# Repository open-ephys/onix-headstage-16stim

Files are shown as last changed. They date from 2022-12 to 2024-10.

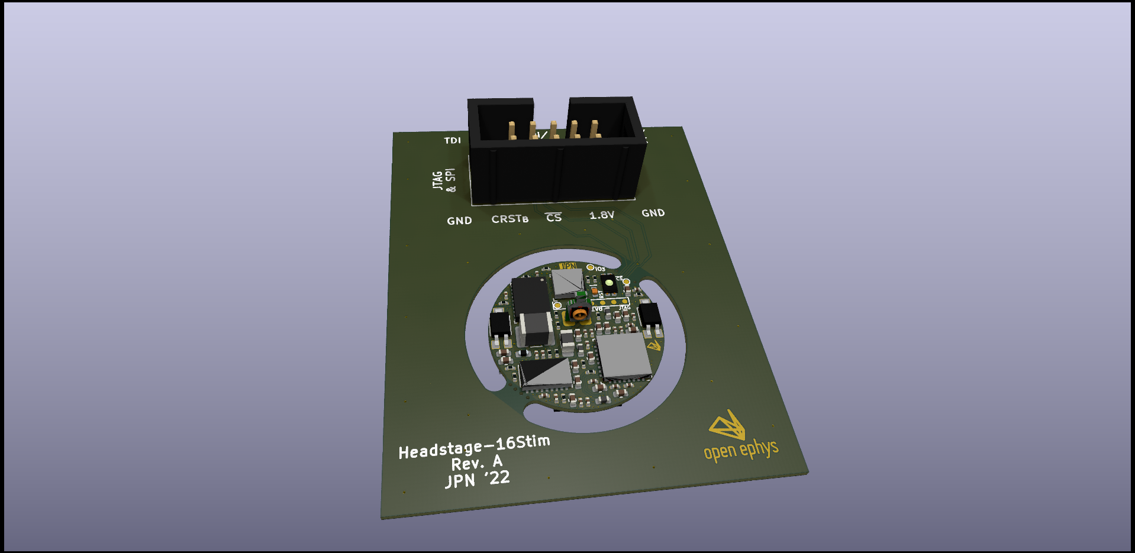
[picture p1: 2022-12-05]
pcb/manufacturing/headstage-16stim-3d-top.png

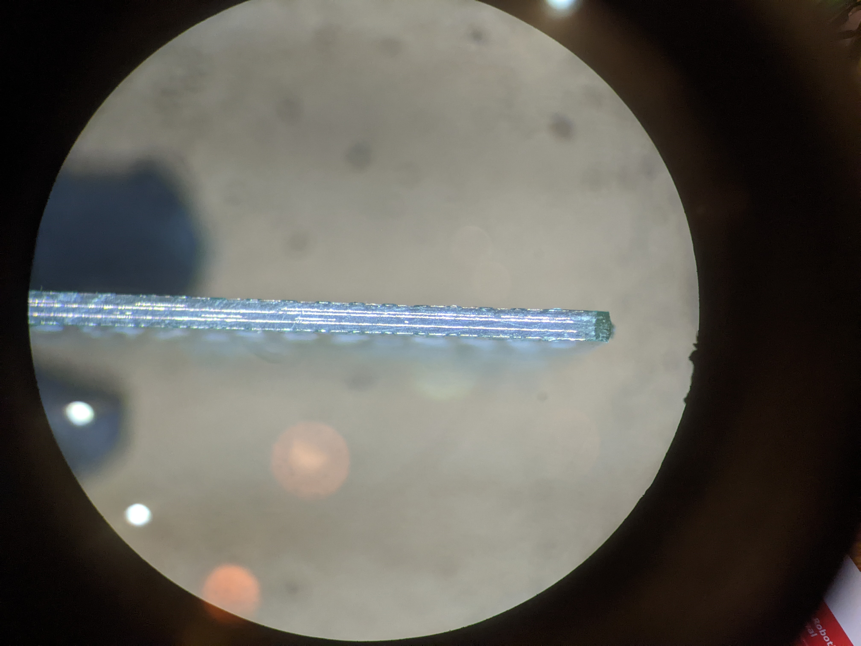
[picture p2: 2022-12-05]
pcb/manufacturing/speedy-6-layer-0.6mm.jpg

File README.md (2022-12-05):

# ONIX 16-Channel Bidirectional Headstage
Serialized, multifunction headstage for wire electrode or silicon probe recordings.

- 16x bi-directional electrophysiology channels (±7V stimulus compliance)
- Integrated stimulus sequencer and memory
- Integrated real-time, room-scale 3D-position tracking
- Integrated absolute orientation tracking

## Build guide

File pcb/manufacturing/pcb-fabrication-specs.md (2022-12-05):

# PCB Fabrication Specifications

## Single board Dimensions
- Width: 40.0000 mm
- Height: 51.0000 mm
- Area: 2040.0000 sq. mm

## Panel
- Fabricator makes panel as 1x5 with V-Cuts
- Fabricator adds frame and fiducial marks
- Fabricator markings allowed on frame

## Stackup
- layer "F.Cu" 
    - type "copper" 
    - Thickness 0.035 mm
- layer "Dielectric 1" 
    - type "prepreg" 
    - Thickness 0.112 mm 
- layer "In1.Cu" 
    - type "copper" 
    - Thickness 0.035 mm
- layer "Dielectric 2" 
    - type "prepreg" 
    - Thickness 0.0329 mm 
- layer "In2.Cu" 
    - type "copper" 
    - Thickness 0.035 mm
- layer "Dielectric 3" 
    - type "core" 
    - Thickness 0.0656 mm 
- layer "In3.Cu" 
    - type "copper" 
    - Thickness 0.035 mm
- layer "Dielectric 4" 
    - type "prepreg" 
    - Thickness 0.0329 mm 
- layer "In4.Cu" 
    - type "copper" 
    - Thickness 0.035 mm
- layer "Dielectric 5" 
    - type "prepreg 
    - Thickness 0.112 mm 
- layer "B.Cu" 
    - type "copper" 
    - Thickness 0.035 mm

- Total thickness: ~0.6mm

## Trace space
- Trace: 0.0762 mm
- Space: 0.0762 mm

## Vias
- Through vias: 232
- Blind/buried: 0
- Micro vias: 0
- VIP
- Vias are epoxy-filled and and plated over

## Drill holes
| Count | Shape |    X Size |    Y Size | Plated | Via/Pad | Start Layer | Stop Layer |
|-------|-------|-----------|-----------|--------|---------|-------------|------------|
|   192 | Round | 0.1000 mm | 0.1000 mm |    PTH |     Via |        F.Cu |       B.Cu |
|    40 | Round | 0.2000 mm | 0.2000 mm |    PTH |     Via |        F.Cu |       B.Cu |
|    10 | Round | 1.0000 mm | 1.0000 mm |    PTH |     Pad |        F.Cu |       B.Cu |

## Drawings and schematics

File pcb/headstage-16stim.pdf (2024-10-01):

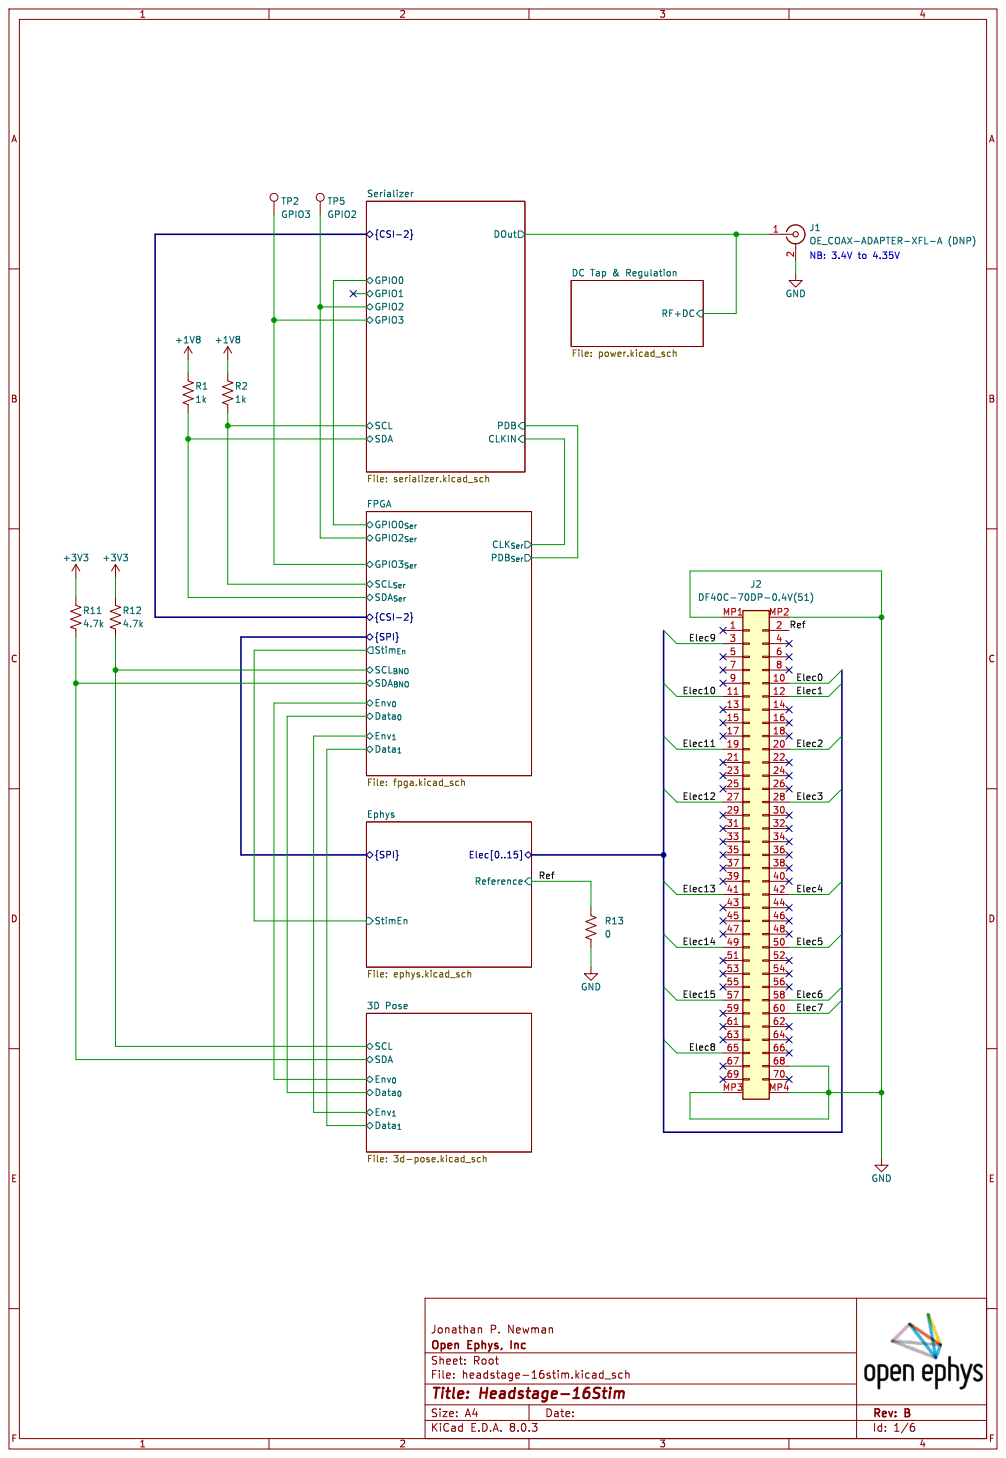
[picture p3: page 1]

{CSI-2} GPIO2 GPIO1 Serializer File: serializer.kicad_sch R11

DC Tap & Regulation File: power.kicad_sch

Data_{1} 3D Pose File: 3d-pose.kicad_sch Reference

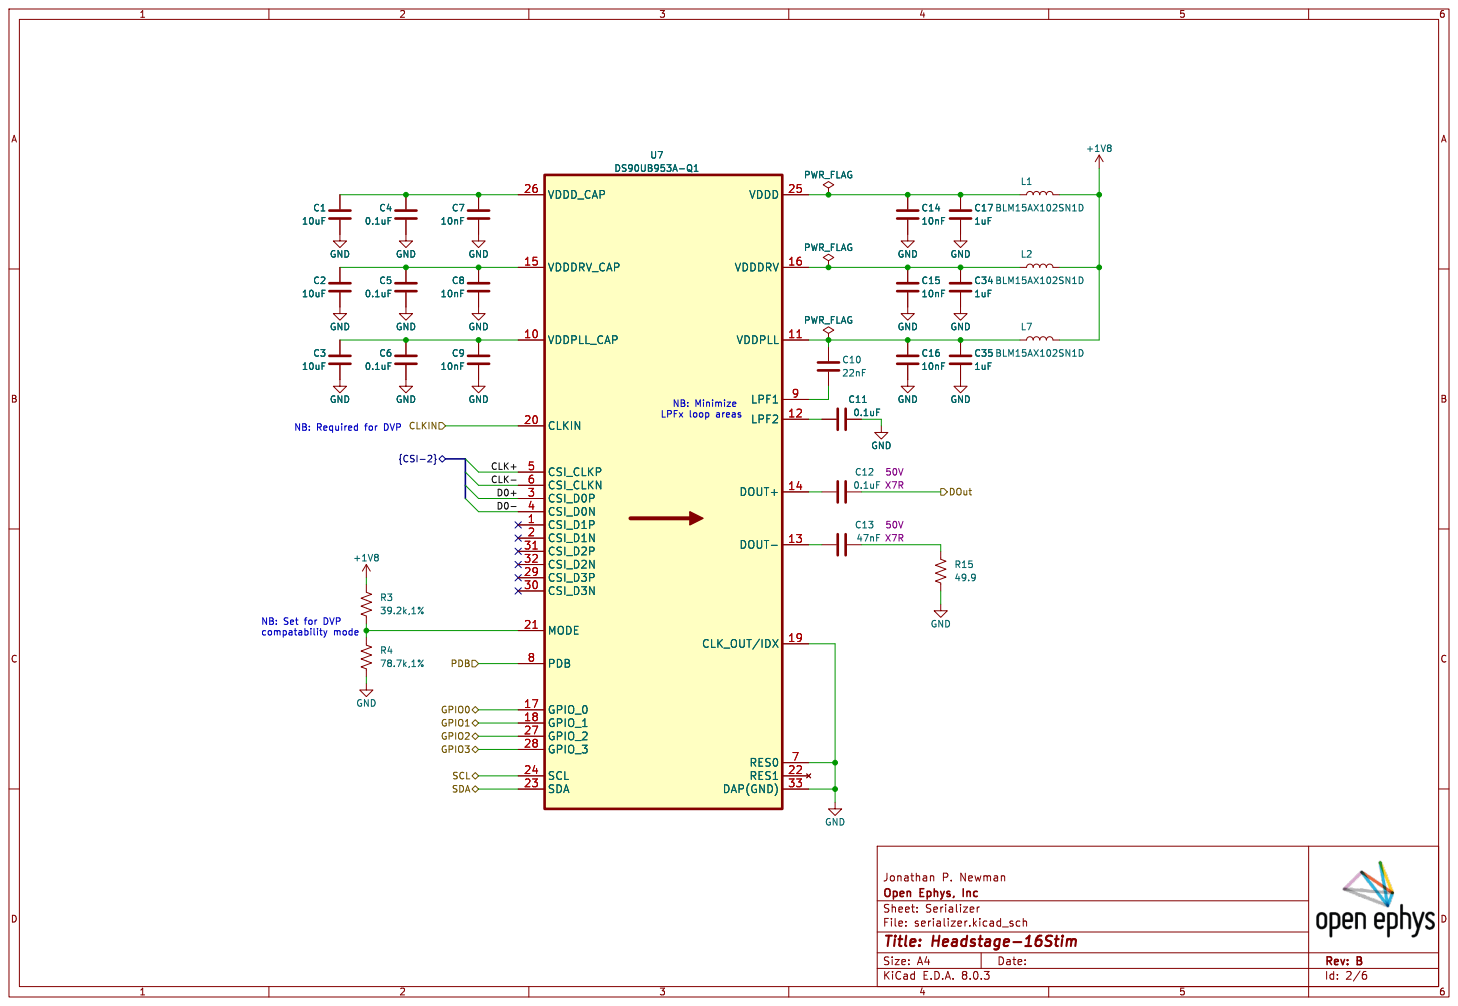
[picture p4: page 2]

LPFx loop areas NB: Set for DVP

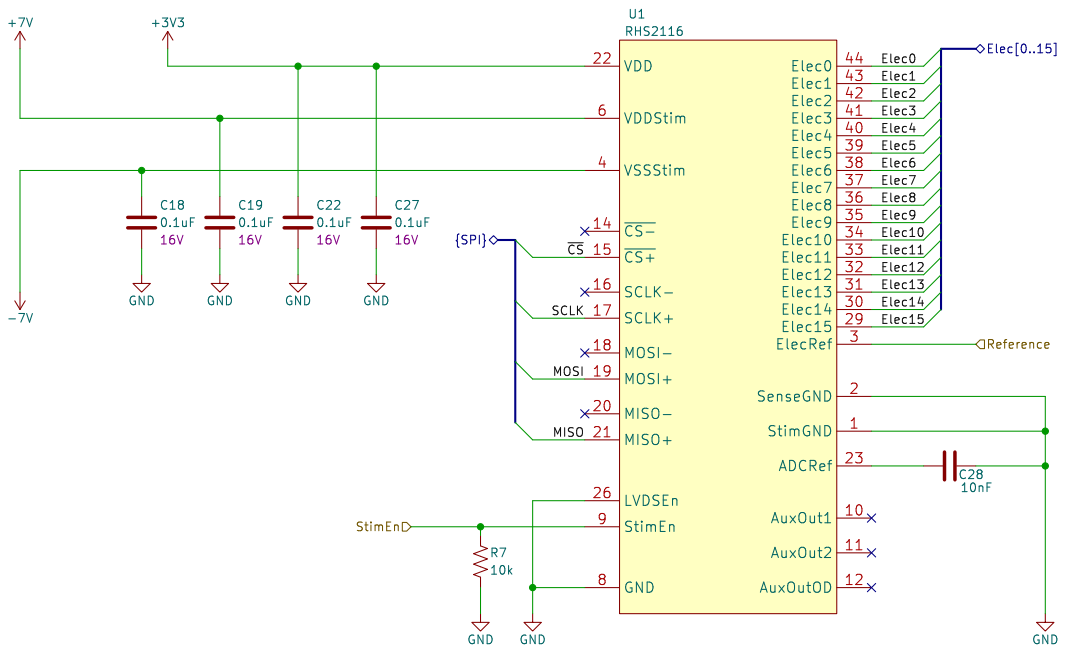
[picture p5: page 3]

File: ephys.kicad_sch Sheet: Ephys
Id: 3/6 Title: Headstage-16Stim

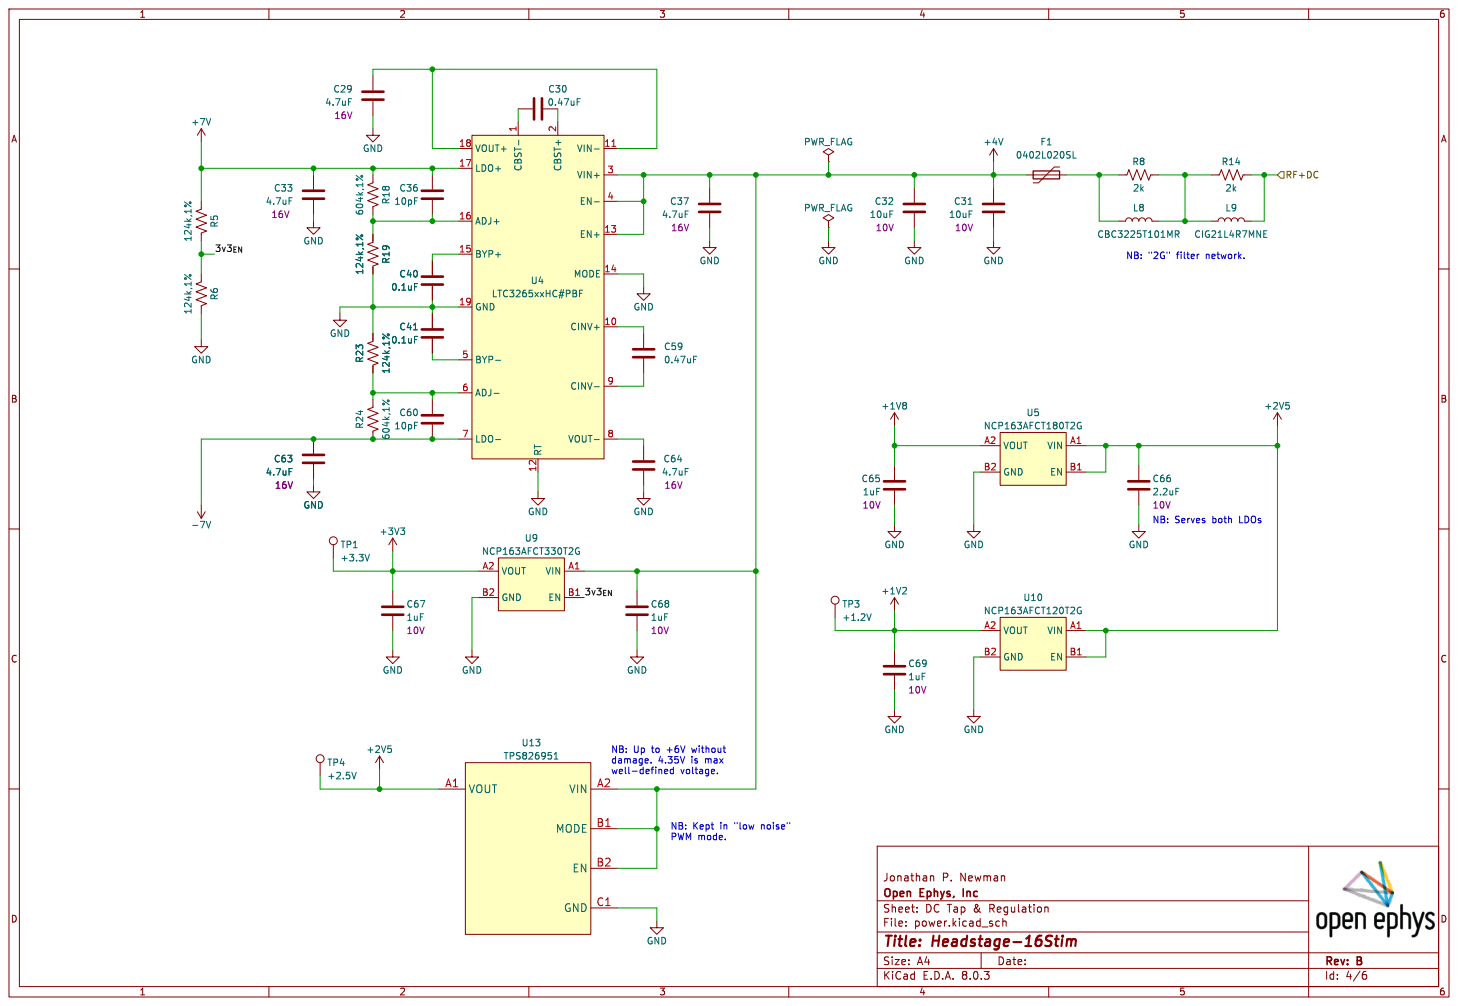
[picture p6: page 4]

2 VIN+ 3 EN- 4 BYP- 5 ADJ- 6

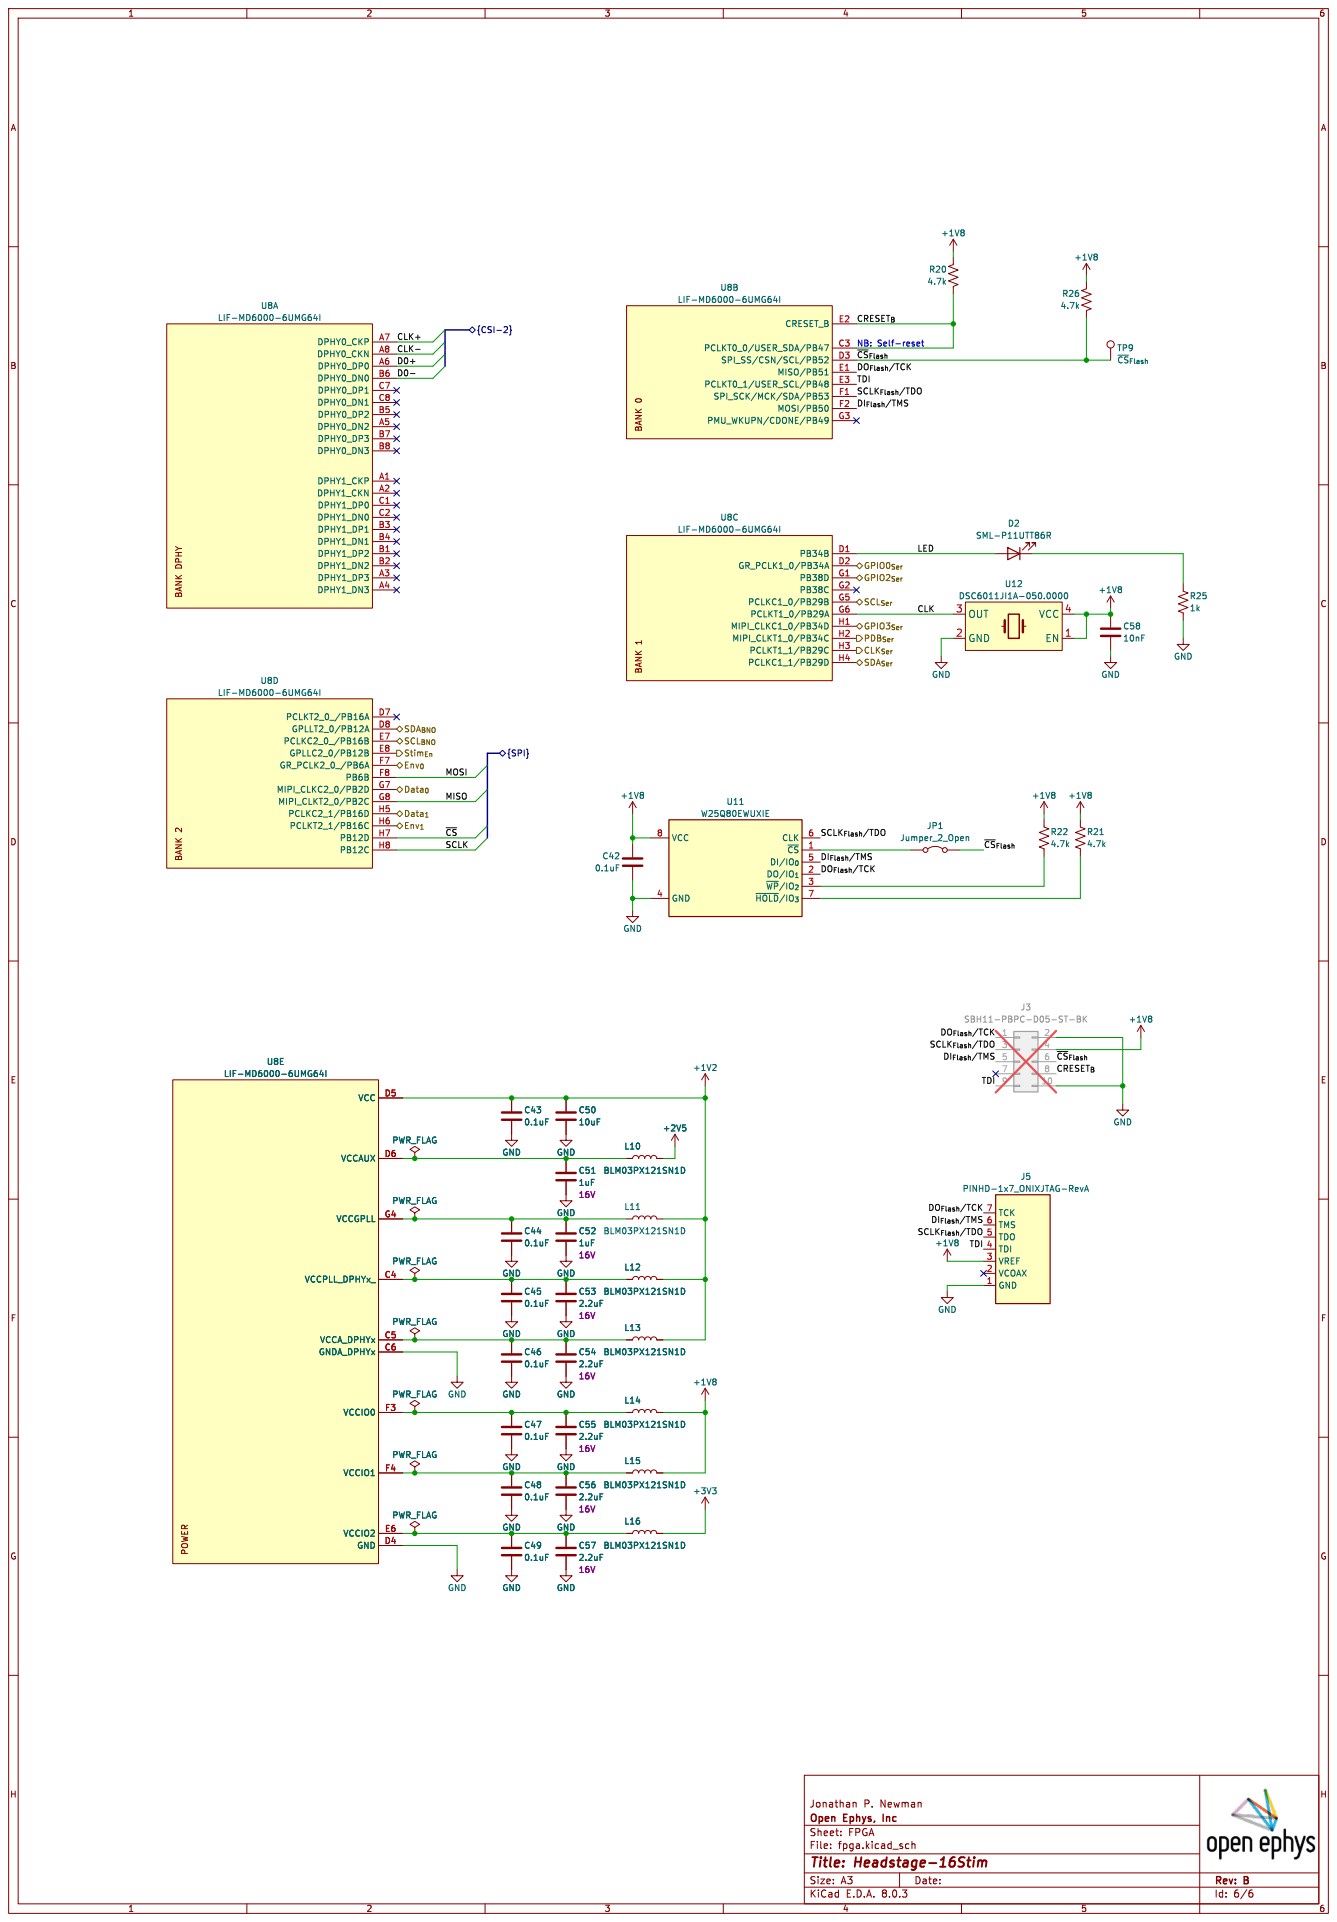
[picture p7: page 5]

CRESET_{B} LED MISO MOSI SCLK

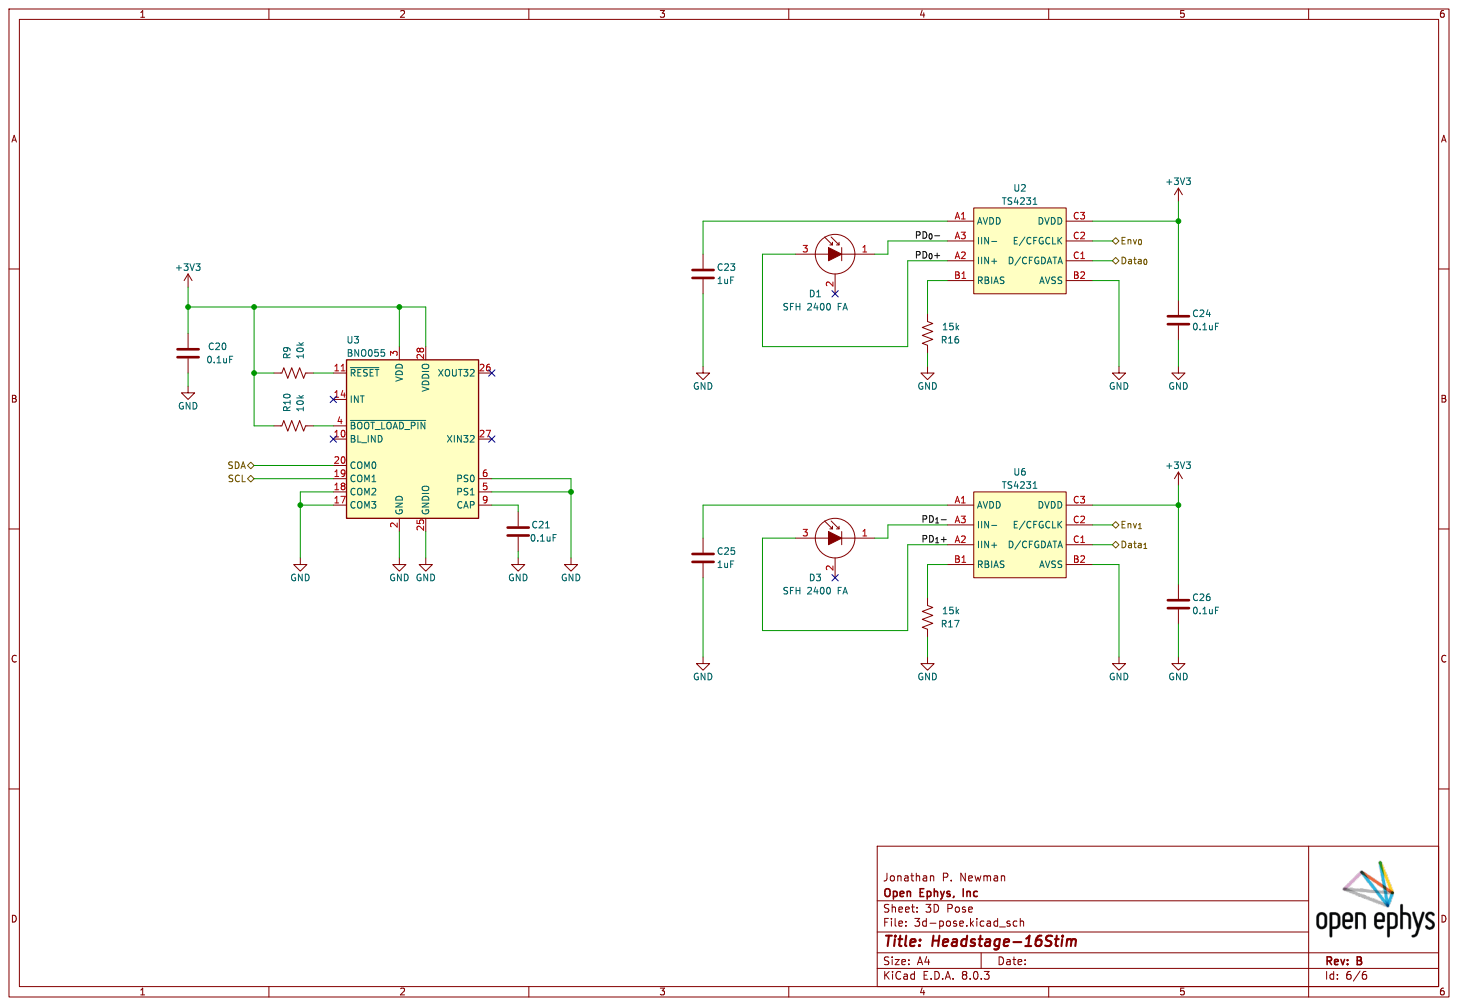
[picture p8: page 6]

3 ~{BOOT_LOAD_PIN} 4 PS1 5 PS0 6 CAP 9 U3BNO055 +3V3 R10 10k GND GND GND GND

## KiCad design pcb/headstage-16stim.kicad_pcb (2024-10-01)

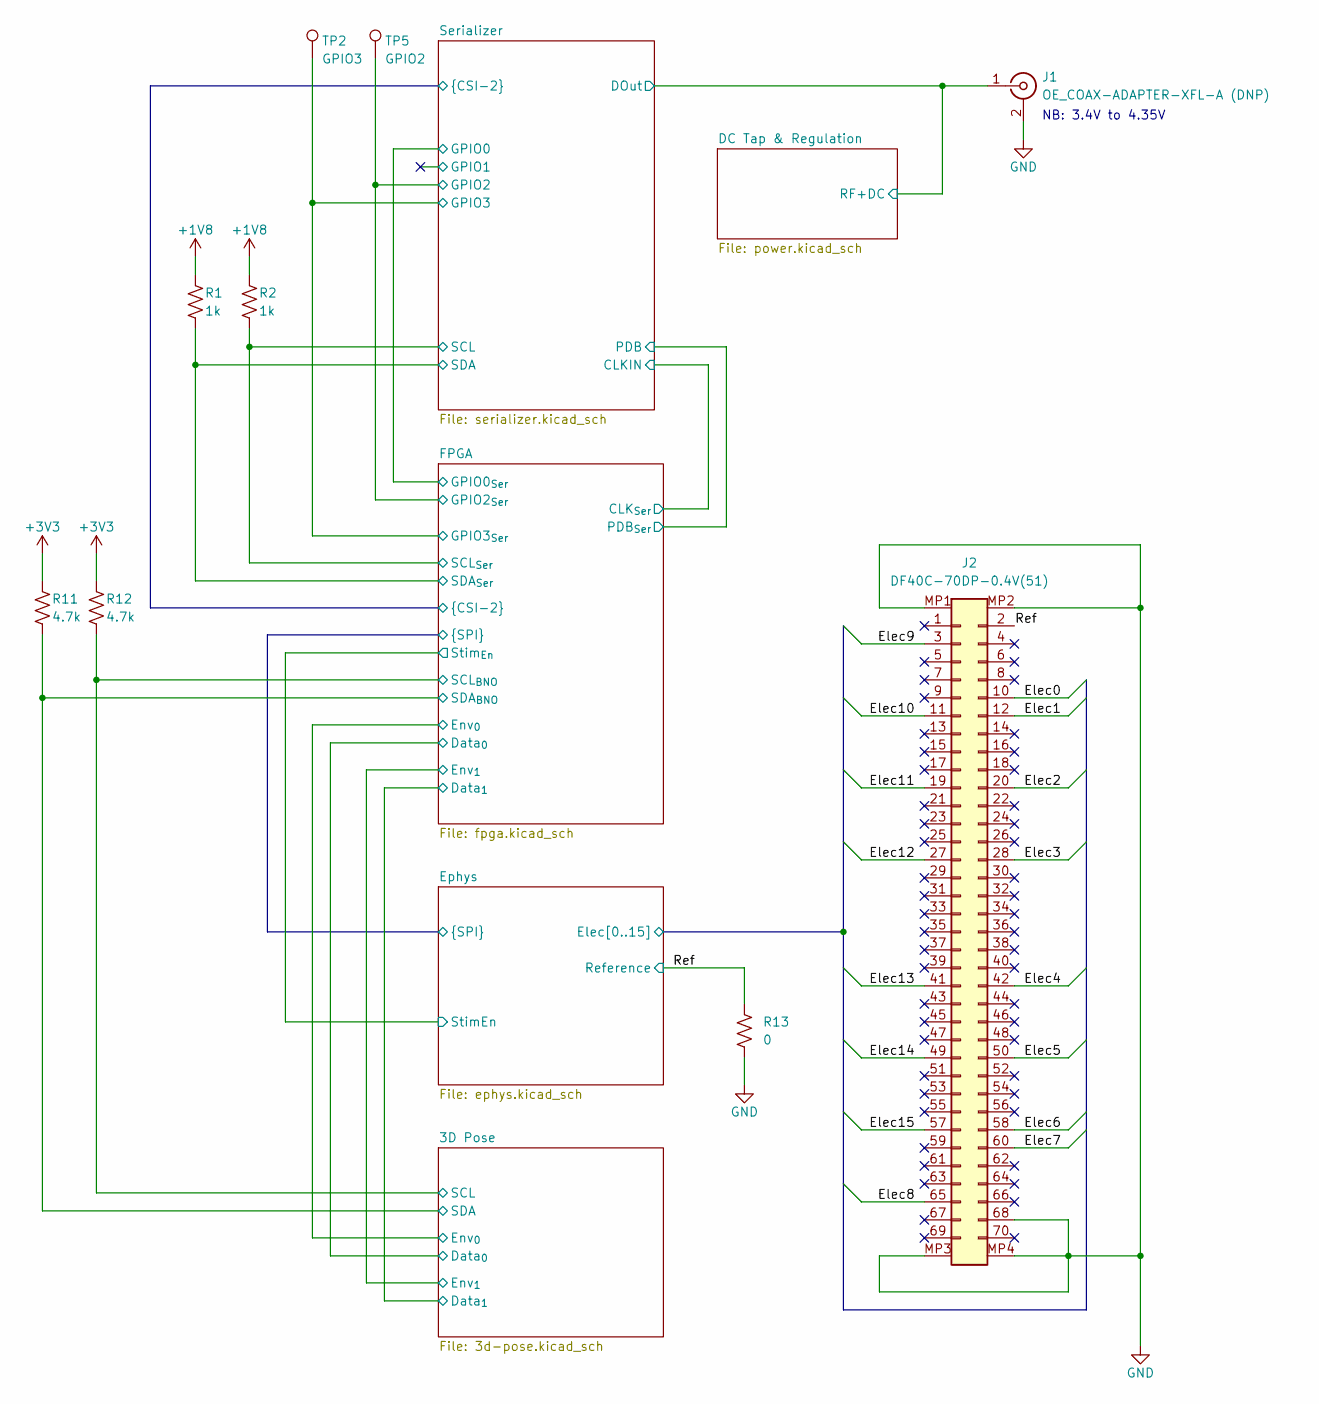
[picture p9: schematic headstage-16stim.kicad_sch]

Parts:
J1: OE_COAX-ADAPTER-XFL-A (DNP); OE_COAX-ADAPTER-XFL-A
J2: DF40C-70DP-0.4V(51); HIROSE_DF40C70DP04V51
R1, R2: 1k; R_0201_0603Metric
R11, R12: 4.7k; R_0201_0603Metric
R13: 0; R_0201_0603Metric
TP2: GPIO3; TestPoint_Pad_D0.6mm
TP5: GPIO2; TestPoint_Pad_D0.6mm

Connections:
+1V8: R1.1, R2.1; also elsewhere on the board
+3V3: R11.1, R12.1; also elsewhere on the board
/3D Pose/SCL: R12.2; also elsewhere on the board
/3D Pose/SDA: R11.2; also elsewhere on the board
/DC Tap & Regulation/RF+DC: J1.1 (In); also elsewhere on the board
/Ephys/Elec0: J2.10; also elsewhere on the board
/Ephys/Elec1: J2.12; also elsewhere on the board
/Ephys/Elec2: J2.20; also elsewhere on the board
/Ephys/Elec3: J2.28; also elsewhere on the board
/Ephys/Elec4: J2.42; also elsewhere on the board
/Ephys/Elec5: J2.50; also elsewhere on the board
/Ephys/Elec6: J2.58; also elsewhere on the board
/Ephys/Elec7: J2.60; also elsewhere on the board
/Ephys/Elec8: J2.65; also elsewhere on the board
/Ephys/Elec9: J2.3; also elsewhere on the board
/Ephys/Elec10: J2.11; also elsewhere on the board
/Ephys/Elec11: J2.19; also elsewhere on the board
/Ephys/Elec12: J2.27; also elsewhere on the board
/Ephys/Elec13: J2.41; also elsewhere on the board
/Ephys/Elec14: J2.49; also elsewhere on the board
/Ephys/Elec15: J2.57; also elsewhere on the board
/FPGA/GPIO2_{Ser}: TP5.1; also elsewhere on the board
/FPGA/GPIO3_{Ser}: TP2.1; also elsewhere on the board
/FPGA/SCL_{Ser}: R2.2; also elsewhere on the board
/FPGA/SDA_{Ser}: R1.2; also elsewhere on the board
/Ref: J2.2, R13.1; also elsewhere on the board
GND: J1.2 (Ext), J2.68, J2.MP1 (MountPin1), J2.MP2 (MountPin2), J2.MP3 (MountPin3), J2.MP4 (MountPin4), R13.2; also elsewhere on the board

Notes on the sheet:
NB: 3.4V to 4.35V

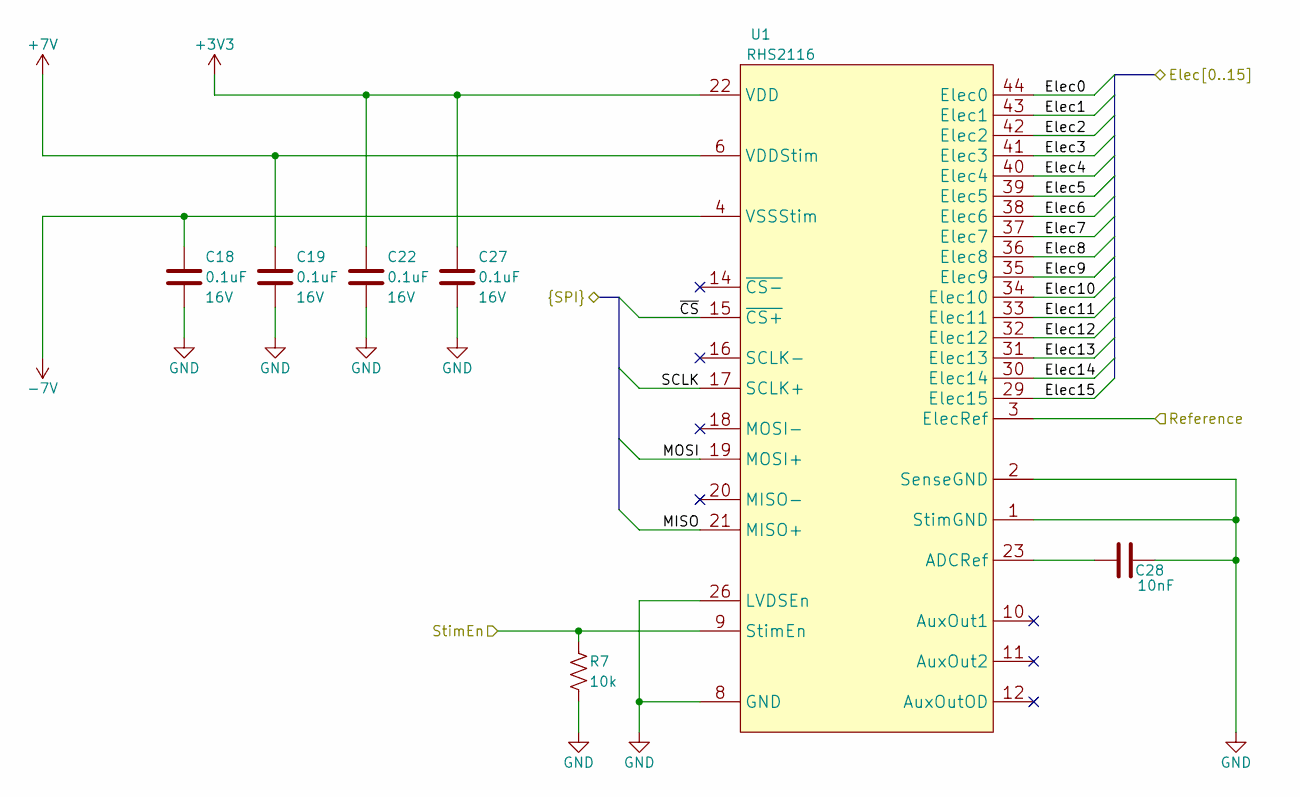
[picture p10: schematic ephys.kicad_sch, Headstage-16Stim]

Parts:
C18, C19, C22, C27: 0.1uF; C_0201_0603Metric; Voltage 16V
C28: 10nF; C_0201_0603Metric; Voltage 35V
R7: 10k; R_0201_0603Metric
U1: RHS2116; INTAN_QFN44-7.0x7.0x0.8_P0.5

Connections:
+3V3: C22.1, C27.1, U1.22 (VDD), U1.27 (VDD), U1.28 (VDD); also elsewhere on the board
+7V: C19.1, U1.6 (VDDStim), U1.7 (VDDStim); also elsewhere on the board
-7V: C18.1, U1.4 (VSSStim), U1.5 (VSSStim), U1.45 (VSSStim); also elsewhere on the board
/Ephys/Elec0: U1.44 (Elec0); also elsewhere on the board
/Ephys/Elec1: U1.43 (Elec1); also elsewhere on the board
/Ephys/Elec2: U1.42 (Elec2); also elsewhere on the board
/Ephys/Elec3: U1.41 (Elec3); also elsewhere on the board
/Ephys/Elec4: U1.40 (Elec4); also elsewhere on the board
/Ephys/Elec5: U1.39 (Elec5); also elsewhere on the board
/Ephys/Elec6: U1.38 (Elec6); also elsewhere on the board
/Ephys/Elec7: U1.37 (Elec7); also elsewhere on the board
/Ephys/Elec8: U1.36 (Elec8); also elsewhere on the board
/Ephys/Elec9: U1.35 (Elec9); also elsewhere on the board
/Ephys/Elec10: U1.34 (Elec10); also elsewhere on the board
/Ephys/Elec11: U1.33 (Elec11); also elsewhere on the board
/Ephys/Elec12: U1.32 (Elec12); also elsewhere on the board
/Ephys/Elec13: U1.31 (Elec13); also elsewhere on the board
/Ephys/Elec14: U1.30 (Elec14); also elsewhere on the board
/Ephys/Elec15: U1.29 (Elec15); also elsewhere on the board
/Ephys/MISO: U1.21 (MISO+); also elsewhere on the board
/Ephys/MOSI: U1.19 (MOSI+); also elsewhere on the board
/Ephys/SCLK: U1.17 (SCLK+); also elsewhere on the board
/Ephys/StimEn: R7.1, U1.9 (StimEn); also elsewhere on the board
/Ephys/~CS: U1.15 (~CS+); also elsewhere on the board
/Ref: U1.3 (ElecRef); also elsewhere on the board
GND: C18.2, C19.2, C22.2, C27.2, C28.2, R7.2, U1.1 (StimGND), U1.2 (SenseGND), U1.8 (GND), U1.13 (GND), U1.24 (GND), U1.25 (GND), U1.26 (LVDSEn); also elsewhere on the board
unnamed: C28.1, U1.23 (ADCRef)

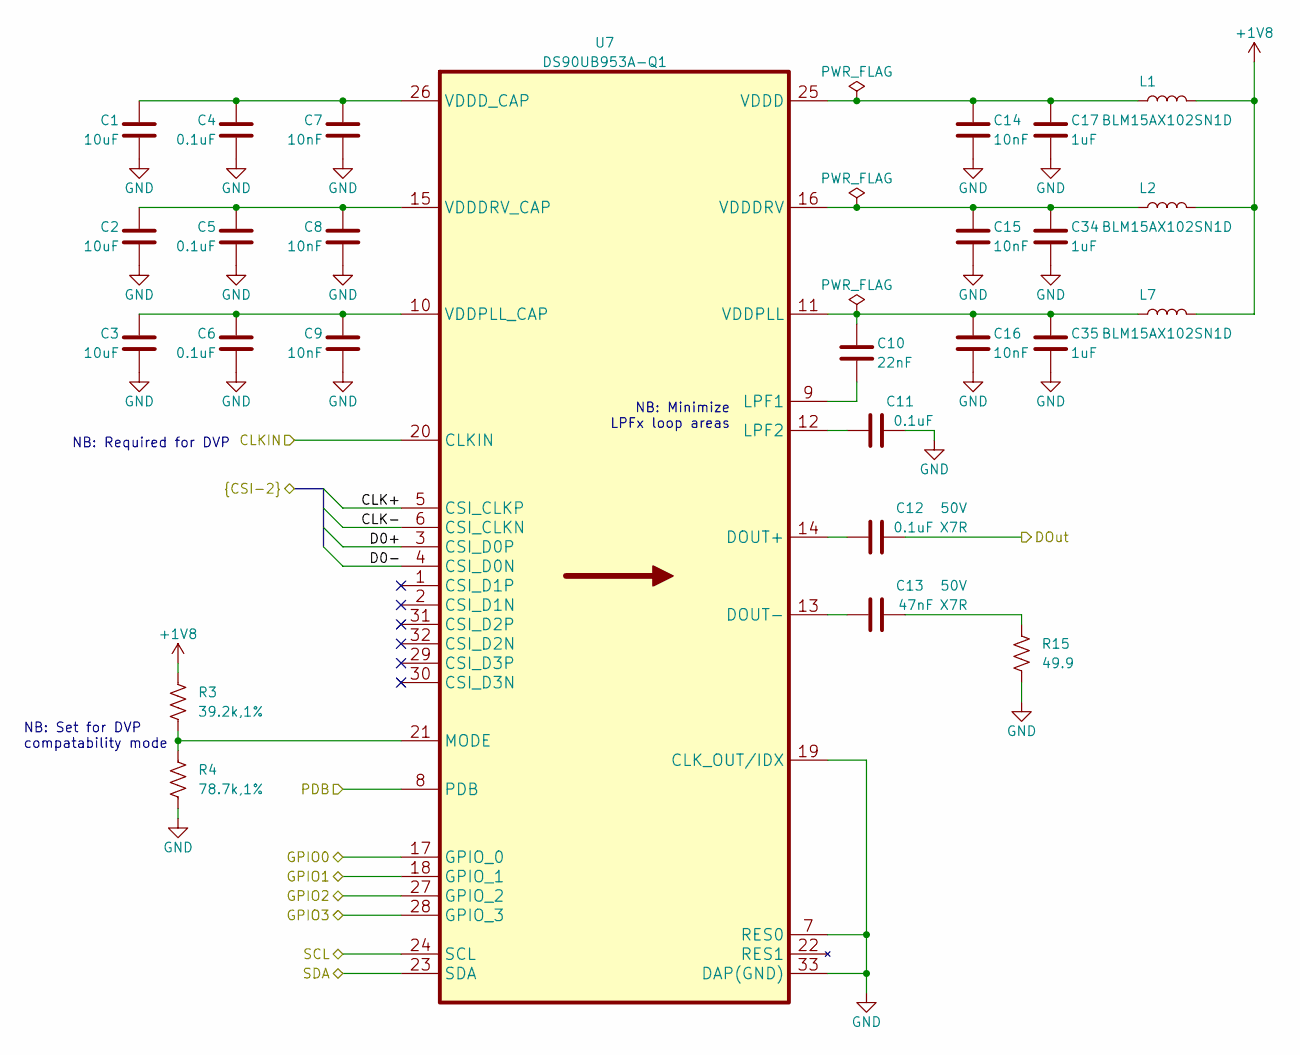
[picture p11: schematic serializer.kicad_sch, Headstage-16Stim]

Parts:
C1, C2, C3: 10uF; C_0402_1005Metric; Voltage 10V
C4, C5, C6, C11: 0.1uF; C_0201_0603Metric; Voltage 16V
C7, C8, C9, C14, C15, C16: 10nF; C_0201_0603Metric; Voltage 35V
C10: 22nF; C_0402_1005Metric; Voltage 35V
C12: 0.1uF; C_0402_1005Metric; Voltage 50V
C13: 47nF; C_0402_1005Metric; Voltage 50V
C17, C34, C35: 1uF; C_0402_1005Metric; Voltage 16V
L1, L2, L7: BLM15AX102SN1D; L_0402_1005Metric
R3: 39.2k,1%; R_0201_0603Metric
R4: 78.7k,1%; R_0201_0603Metric
R15: 49.9; R_0201_0603Metric
U7: DS90UB953A-Q1; TI_RHB0032P

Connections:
+1V8: L1.2, L2.2, L7.2, R3.1; also elsewhere on the board
/DC Tap & Regulation/RF+DC: C12.2; also elsewhere on the board
/FPGA/CLK+: U7.5 (CSI_CLKP); also elsewhere on the board
/FPGA/CLK-: U7.6 (CSI_CLKN); also elsewhere on the board
/FPGA/CLK_{Ser}: U7.20 (CLKIN); also elsewhere on the board
/FPGA/D0+: U7.3 (CSI_D0P); also elsewhere on the board
/FPGA/D0-: U7.4 (CSI_D0N); also elsewhere on the board
/FPGA/GPIO0_{Ser}: U7.17 (GPIO_0); also elsewhere on the board
/FPGA/GPIO2_{Ser}: U7.27 (GPIO_2); also elsewhere on the board
/FPGA/GPIO3_{Ser}: U7.28 (GPIO_3); also elsewhere on the board
/FPGA/PDB_{Ser}: U7.8 (PDB); also elsewhere on the board
/FPGA/SCL_{Ser}: U7.24 (SCL); also elsewhere on the board
/FPGA/SDA_{Ser}: U7.23 (SDA); also elsewhere on the board
/Serializer/GPIO1: U7.18 (GPIO_1)
GND: C1.2, C2.2, C3.2, C4.2, C5.2, C6.2, C7.2, C8.2, C9.2, C11.2, C14.2, C15.2, C16.2, C17.2, C34.2, C35.2, R4.2, R15.2, U7.7 (RES0), U7.19 (CLK_OUT/IDX), U7.33 (DAP(GND)); also elsewhere on the board
unnamed: C13.2, R15.1
unnamed: C12.1, U7.14 (DOUT+)
unnamed: C13.1, U7.13 (DOUT-)
unnamed: C10.2, U7.9 (LPF1)
unnamed: C11.1, U7.12 (LPF2)
unnamed: R3.2, R4.1, U7.21 (MODE)
unnamed: C14.1, C17.1, L1.1, U7.25 (VDDD)
unnamed: C15.1, C34.1, L2.1, U7.16 (VDDDRV)
unnamed: C2.1, C5.1, C8.1, U7.15 (VDDDRV_CAP)
unnamed: C1.1, C4.1, C7.1, U7.26 (VDDD_CAP)
unnamed: C10.1, C16.1, C35.1, L7.1, U7.11 (VDDPLL)
unnamed: C3.1, C6.1, C9.1, U7.10 (VDDPLL_CAP)

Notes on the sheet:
NB: Set for DVP compatability mode
NB: Required for DVP
NB: Minimize LPFx loop areas

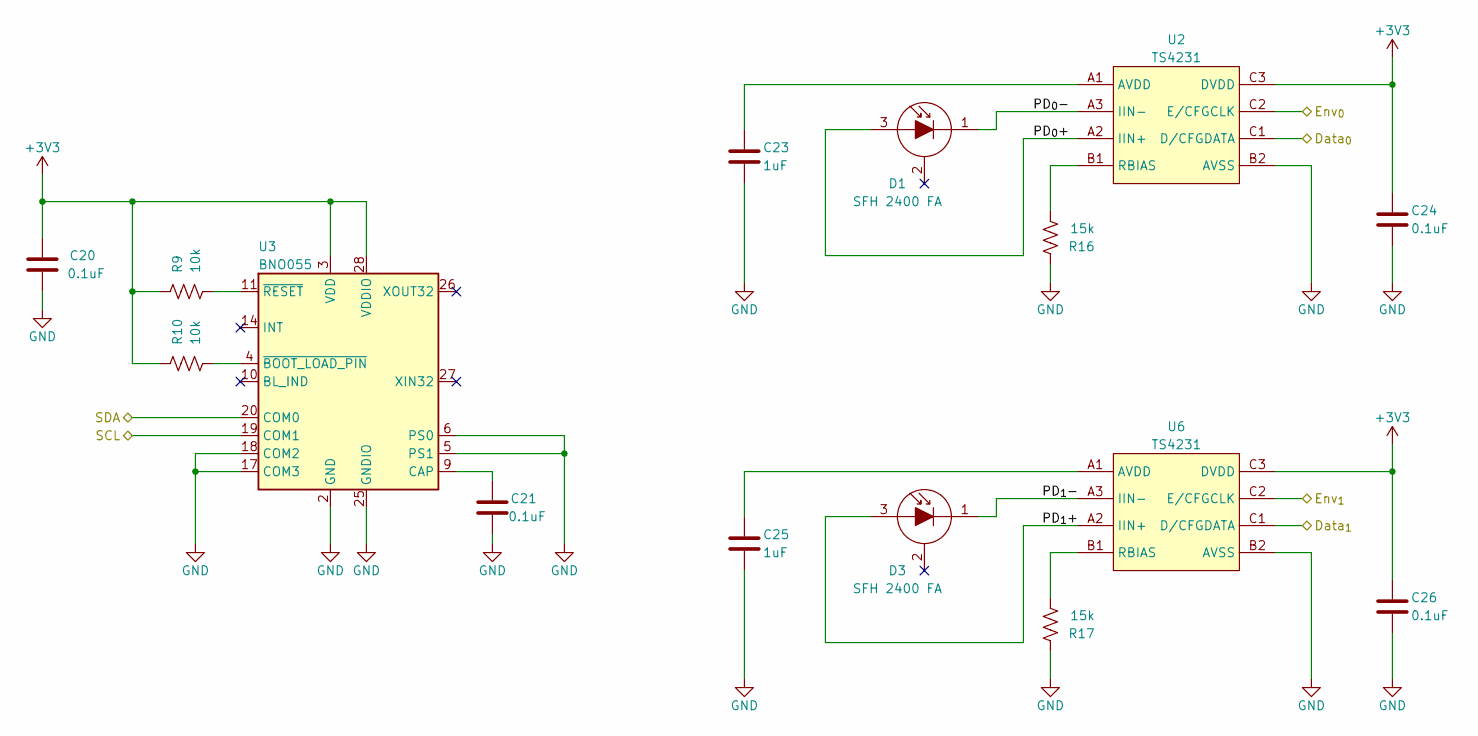
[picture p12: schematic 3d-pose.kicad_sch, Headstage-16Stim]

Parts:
C20, C21, C24, C26: 0.1uF; C_0201_0603Metric; Voltage 16V
C23, C25: 1uF; C_0402_1005Metric; Voltage 16V
D1, D3: SFH 2400 FA; OSRAM_SFH2400FA-Tight
R9, R10: 10k; R_0201_0603Metric
R16, R17: 15k; R_0201_0603Metric
U2, U6: TS4231; TRIAD_BGA-9_3x3_1.7x1.7mm
U3: BNO055; LGA-28_5.2x3.8mm_P0.5mm

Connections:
+3V3: C20.2, C24.2, C26.2, R9.1, R10.1, U2.C3 (DVDD), U3.3 (VDD), U3.28 (VDDIO), U6.C3 (DVDD); also elsewhere on the board
/3D Pose/Data_{0}: U2.C1 (D/CFGDATA); also elsewhere on the board
/3D Pose/Data_{1}: U6.C1 (D/CFGDATA); also elsewhere on the board
/3D Pose/Env_{0}: U2.C2 (E/CFGCLK); also elsewhere on the board
/3D Pose/Env_{1}: U6.C2 (E/CFGCLK); also elsewhere on the board
/3D Pose/PD_{0}+: D1.3 (A), U2.A2 (IIN+)
/3D Pose/PD_{0}-: D1.1 (K), U2.A3 (IIN-)
/3D Pose/PD_{1}+: D3.3 (A), U6.A2 (IIN+)
/3D Pose/PD_{1}-: D3.1 (K), U6.A3 (IIN-)
/3D Pose/SCL: U3.19 (COM1); also elsewhere on the board
/3D Pose/SDA: U3.20 (COM0); also elsewhere on the board
GND: C20.1, C21.1, C23.2, C24.1, C25.2, C26.1, R16.1, R17.1, U2.B2 (AVSS), U2.B3 (AVSS), U3.2 (GND), U3.5 (PS1), U3.6 (PS0), U3.15 (GNDIO), U3.16 (GNDIO), U3.17 (COM3), U3.18 (COM2), U3.25 (GNDIO), U6.B2 (AVSS), U6.B3 (AVSS); also elsewhere on the board
unnamed: C23.1, U2.A1 (AVDD)
unnamed: R16.2, U2.B1 (RBIAS)
unnamed: C21.2, U3.9 (CAP)
unnamed: R10.2, U3.4 (~BOOT_LOAD_PIN)
unnamed: R9.2, U3.11 (~RESET)
unnamed: C25.1, U6.A1 (AVDD)
unnamed: R17.2, U6.B1 (RBIAS)

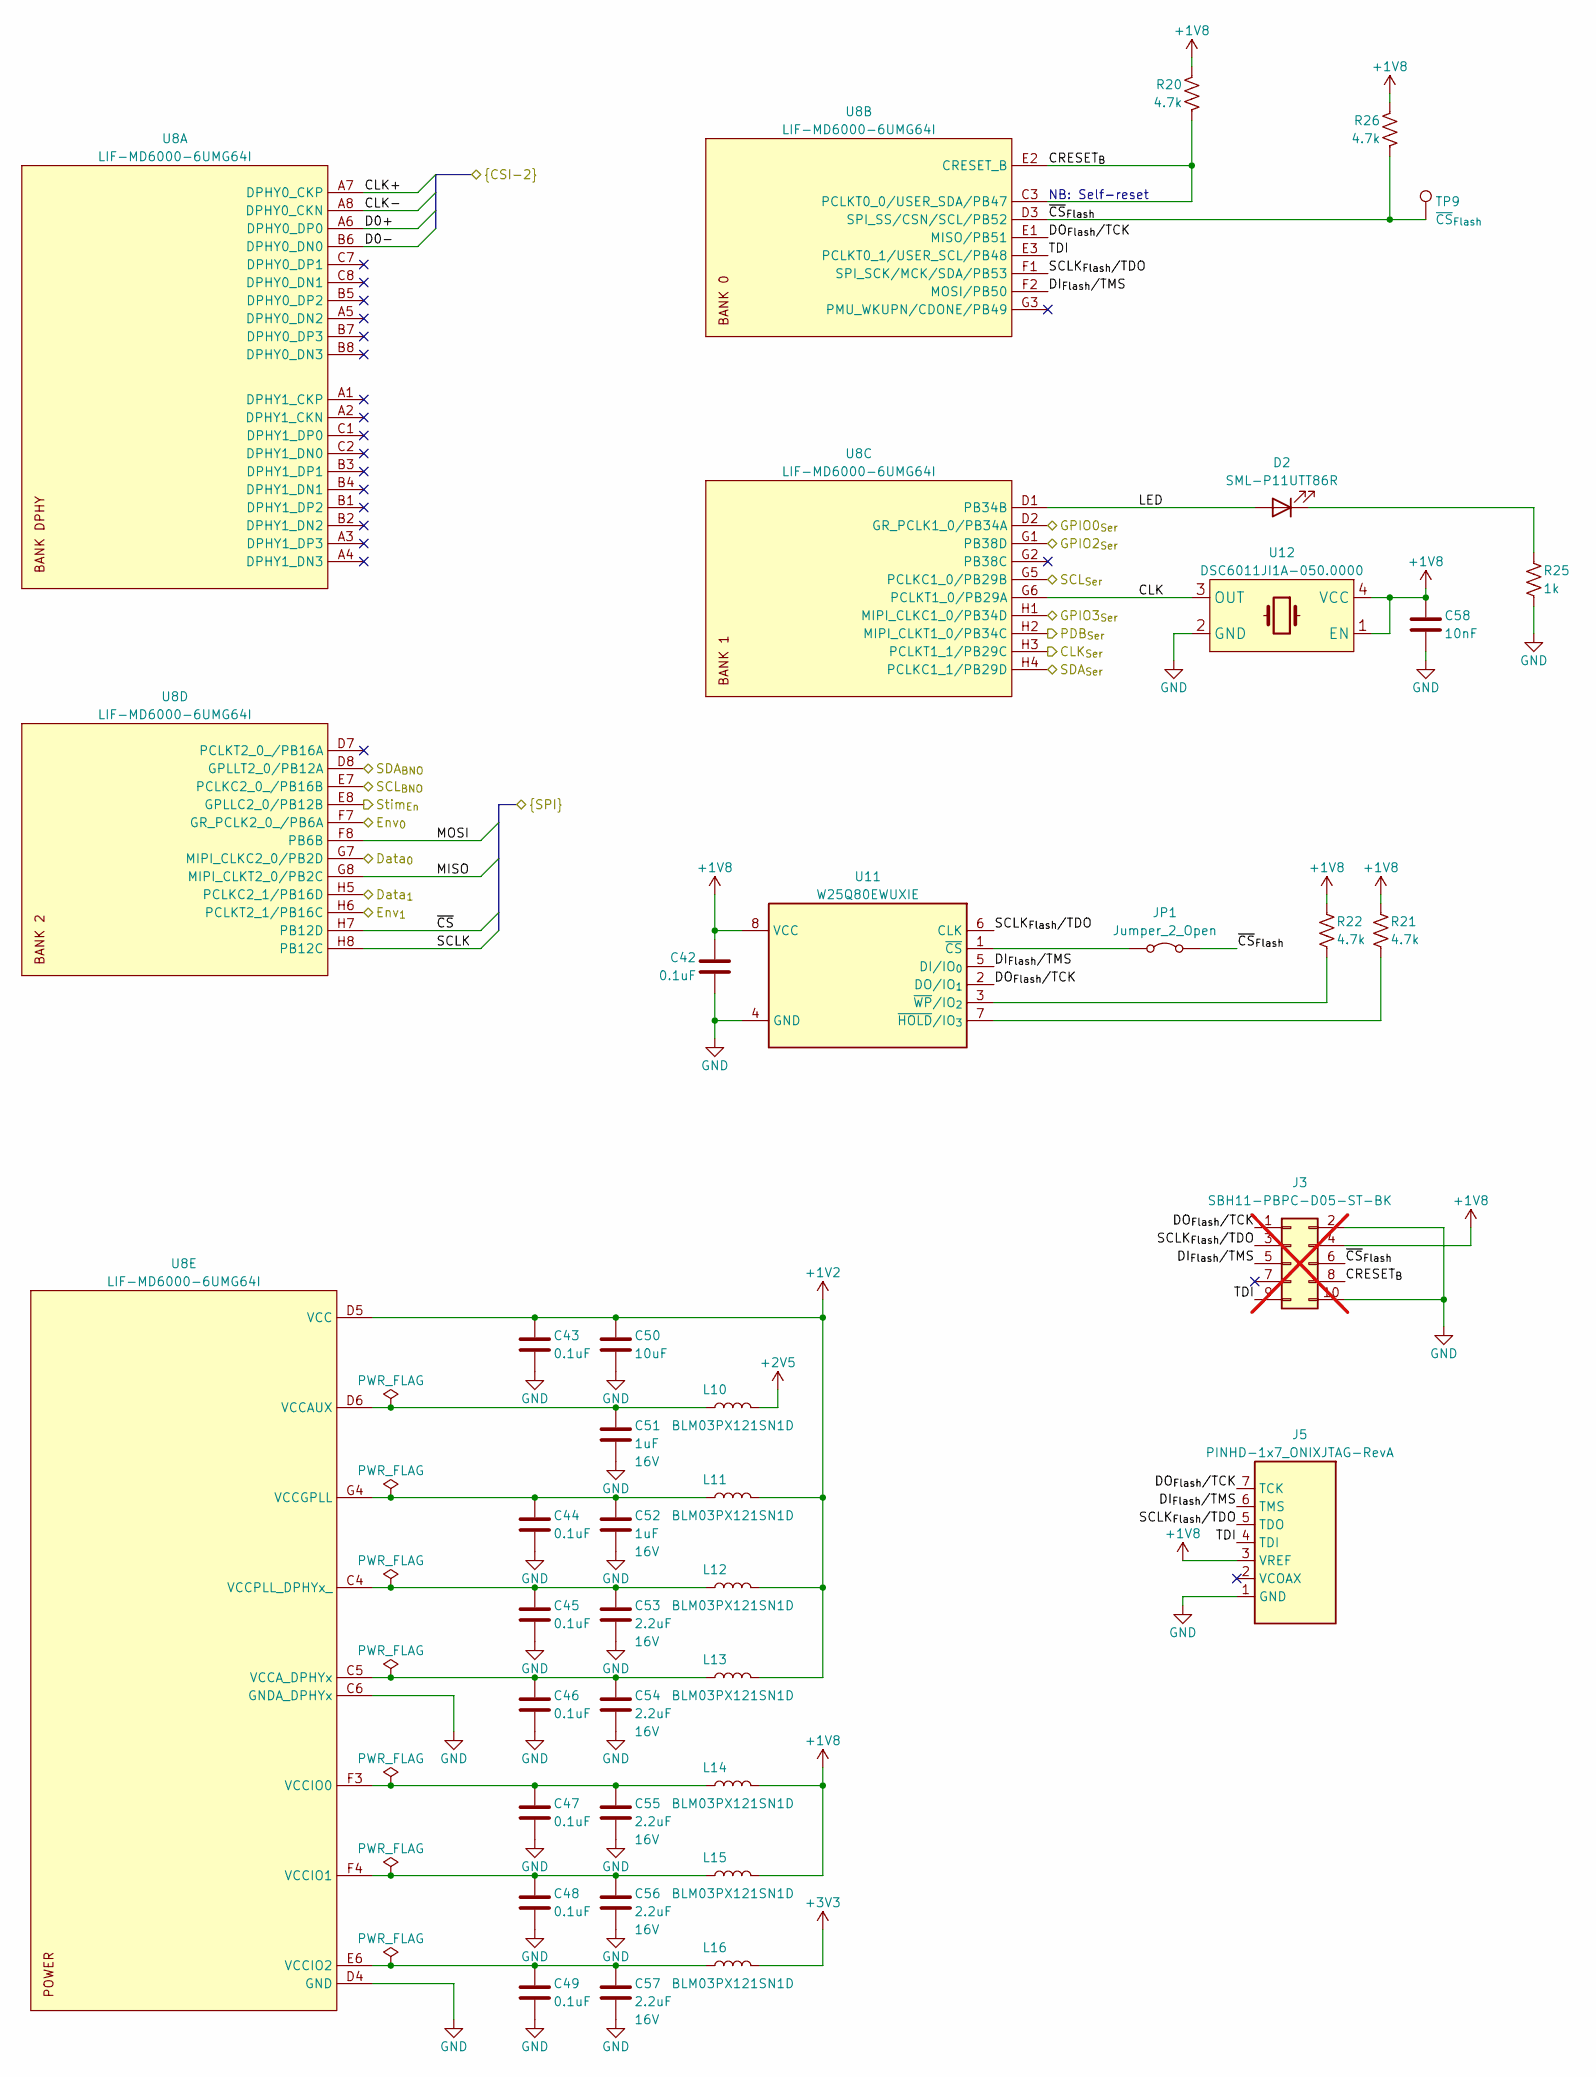
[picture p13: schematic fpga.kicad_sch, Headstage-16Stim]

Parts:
C42, C43, C44, C45, C46, C47, C48, C49: 0.1uF; C_0201_0603Metric; Voltage 16V
C50: 10uF; C_0402_1005Metric; Voltage 10V
C51, C52: 1uF; C_0402_1005Metric; Voltage 16V
C53, C54, C55, C56, C57: 2.2uF; C_0402_1005Metric; Voltage 16V
C58: 10nF; C_0201_0603Metric; Voltage 35V
D2: SML-P11UTT86R; ROHM_SML-P11MTT86R
J3: SBH11-PBPC-D05-ST-BK; IDC-Header_2x05_P2.54mm_Vertical; not fitted
J5: PINHD-1x7_ONIXJTAG-RevA; ONIXJTAG-RevA
JP1: Jumper_2_Open; OE_SolderJumper-2_0201_Open_Pad
L10, L11, L12, L13, L14, L15, L16: BLM03PX121SN1D; L_0201_0603Metric
R20, R21, R22, R26: 4.7k; R_0201_0603Metric
R25: 1k; R_0201_0603Metric
TP9: ~{CS}_{Flash}; TestPoint_Pad_D0.6mm
U8: LIF-MD6000-6UMG64I; LATTICE_ufcBGA64C40P8X8_3.5X3.5X1.0
U11: W25Q80EWUXIE; WINBOND_USON8-2x3x0.6
U12: DSC6011JI1A-050.0000; MICROCHIP_VFLGA4-2.0x1.6

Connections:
+1V2: C43.1, C50.1, L11.2, L12.2, L13.2, U8.D5 (VCC), U8.E4 (VCC); also elsewhere on the board
+1V8: C42.1, C58.1, J3.4, J5.3 (VREF), L14.2, L15.2, R20.1, R21.1, R22.1, R26.1, U11.8 (VCC), U12.1 (EN), U12.4 (VCC); also elsewhere on the board
+2V5: L10.2; also elsewhere on the board
+3V3: L16.2; also elsewhere on the board
/3D Pose/Data_{0}: U8.G7 (MIPI_CLKC2_0/PB2D); also elsewhere on the board
/3D Pose/Data_{1}: U8.H5 (PCLKC2_1/PB16D); also elsewhere on the board
/3D Pose/Env_{0}: U8.F7 (GR_PCLK2_0_/PB6A); also elsewhere on the board
/3D Pose/Env_{1}: U8.H6 (PCLKT2_1/PB16C); also elsewhere on the board
/3D Pose/SCL: U8.E7 (PCLKC2_0_/PB16B); also elsewhere on the board
/3D Pose/SDA: U8.D8 (GPLLT2_0/PB12A); also elsewhere on the board
/Ephys/MISO: U8.G8 (MIPI_CLKT2_0/PB2C); also elsewhere on the board
/Ephys/MOSI: U8.F8 (PB6B); also elsewhere on the board
/Ephys/SCLK: U8.H8 (PB12C); also elsewhere on the board
/Ephys/StimEn: U8.E8 (GPLLC2_0/PB12B); also elsewhere on the board
/Ephys/~CS: U8.H7 (PB12D); also elsewhere on the board
/FPGA/CLK: U8.G6 (PCLKT1_0/PB29A), U12.3 (OUT)
/FPGA/CLK+: U8.A7 (DPHY0_CKP); also elsewhere on the board
/FPGA/CLK-: U8.A8 (DPHY0_CKN); also elsewhere on the board
/FPGA/CLK_{Ser}: U8.H3 (PCLKT1_1/PB29C); also elsewhere on the board
/FPGA/CRESET_{B}: J3.8, R20.2, U8.C3 (PCLKT0_0/USER_SDA/PB47), U8.E2 (CRESET_B)
/FPGA/D0+: U8.A6 (DPHY0_DP0); also elsewhere on the board
/FPGA/D0-: U8.B6 (DPHY0_DN0); also elsewhere on the board
/FPGA/DI_{Flash}/TMS: J3.5, J5.6 (TMS), U8.F2 (MOSI/PB50), U11.5 (DI/IO_{0})
/FPGA/DO_{Flash}/TCK: J3.1, J5.7 (TCK), U8.E1 (MISO/PB51), U11.2 (DO/IO_{1})
/FPGA/GPIO0_{Ser}: U8.D2 (GR_PCLK1_0/PB34A); also elsewhere on the board
/FPGA/GPIO2_{Ser}: U8.G1 (PB38D); also elsewhere on the board
/FPGA/GPIO3_{Ser}: U8.H1 (MIPI_CLKC1_0/PB34D); also elsewhere on the board
/FPGA/LED: D2.2 (A), U8.D1 (PB34B)
/FPGA/PDB_{Ser}: U8.H2 (MIPI_CLKT1_0/PB34C); also elsewhere on the board
/FPGA/SCLK_{Flash}/TDO: J3.3, J5.5 (TDO), U8.F1 (SPI_SCK/MCK/SDA/PB53), U11.6 (CLK)
/FPGA/SCL_{Ser}: U8.G5 (PCLKC1_0/PB29B); also elsewhere on the board
/FPGA/SDA_{Ser}: U8.H4 (PCLKC1_1/PB29D); also elsewhere on the board
/FPGA/TDI: J3.9, J5.4 (TDI), U8.E3 (PCLKT0_1/USER_SCL/PB48)
/FPGA/~CS_{Flash}: J3.6, JP1.2 (B), R26.2, TP9.1, U8.D3 (SPI_SS/CSN/SCL/PB52)
GND: C42.2, C43.2, C44.2, C45.2, C46.2, C47.2, C48.2, C49.2, C50.2, C51.2, C52.2, C53.2, C54.2, C55.2, C56.2, C57.2, C58.2, J3.2, J3.10, J5.1 (GND), R25.2, U8.C6 (GNDA_DPHYx), U8.D4 (GND), U8.E5 (GND), U8.F5 (GND), U11.4 (GND), U11.9 (GND), U12.2 (GND); also elsewhere on the board
unnamed: C49.1, C57.1, L16.1, U8.E6 (VCCIO2), U8.F6 (VCCIO2)
unnamed: D2.1 (K), R25.1
unnamed: JP1.1 (A), U11.1 (~CS)
unnamed: C51.1, L10.1, U8.D6 (VCCAUX)
unnamed: C46.1, C54.1, L13.1, U8.C5 (VCCA_DPHYx)
unnamed: C44.1, C52.1, L11.1, U8.G4 (VCCGPLL)
unnamed: C47.1, C55.1, L14.1, U8.F3 (VCCIO0)
unnamed: C48.1, C56.1, L15.1, U8.F4 (VCCIO1)
unnamed: C45.1, C53.1, L12.1, U8.C4 (VCCPLL_DPHYx_)
unnamed: R21.2, U11.7 (~HOLD/IO_{3})
unnamed: R22.2, U11.3 (~WP/IO_{2})

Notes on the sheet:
NB: Self-reset

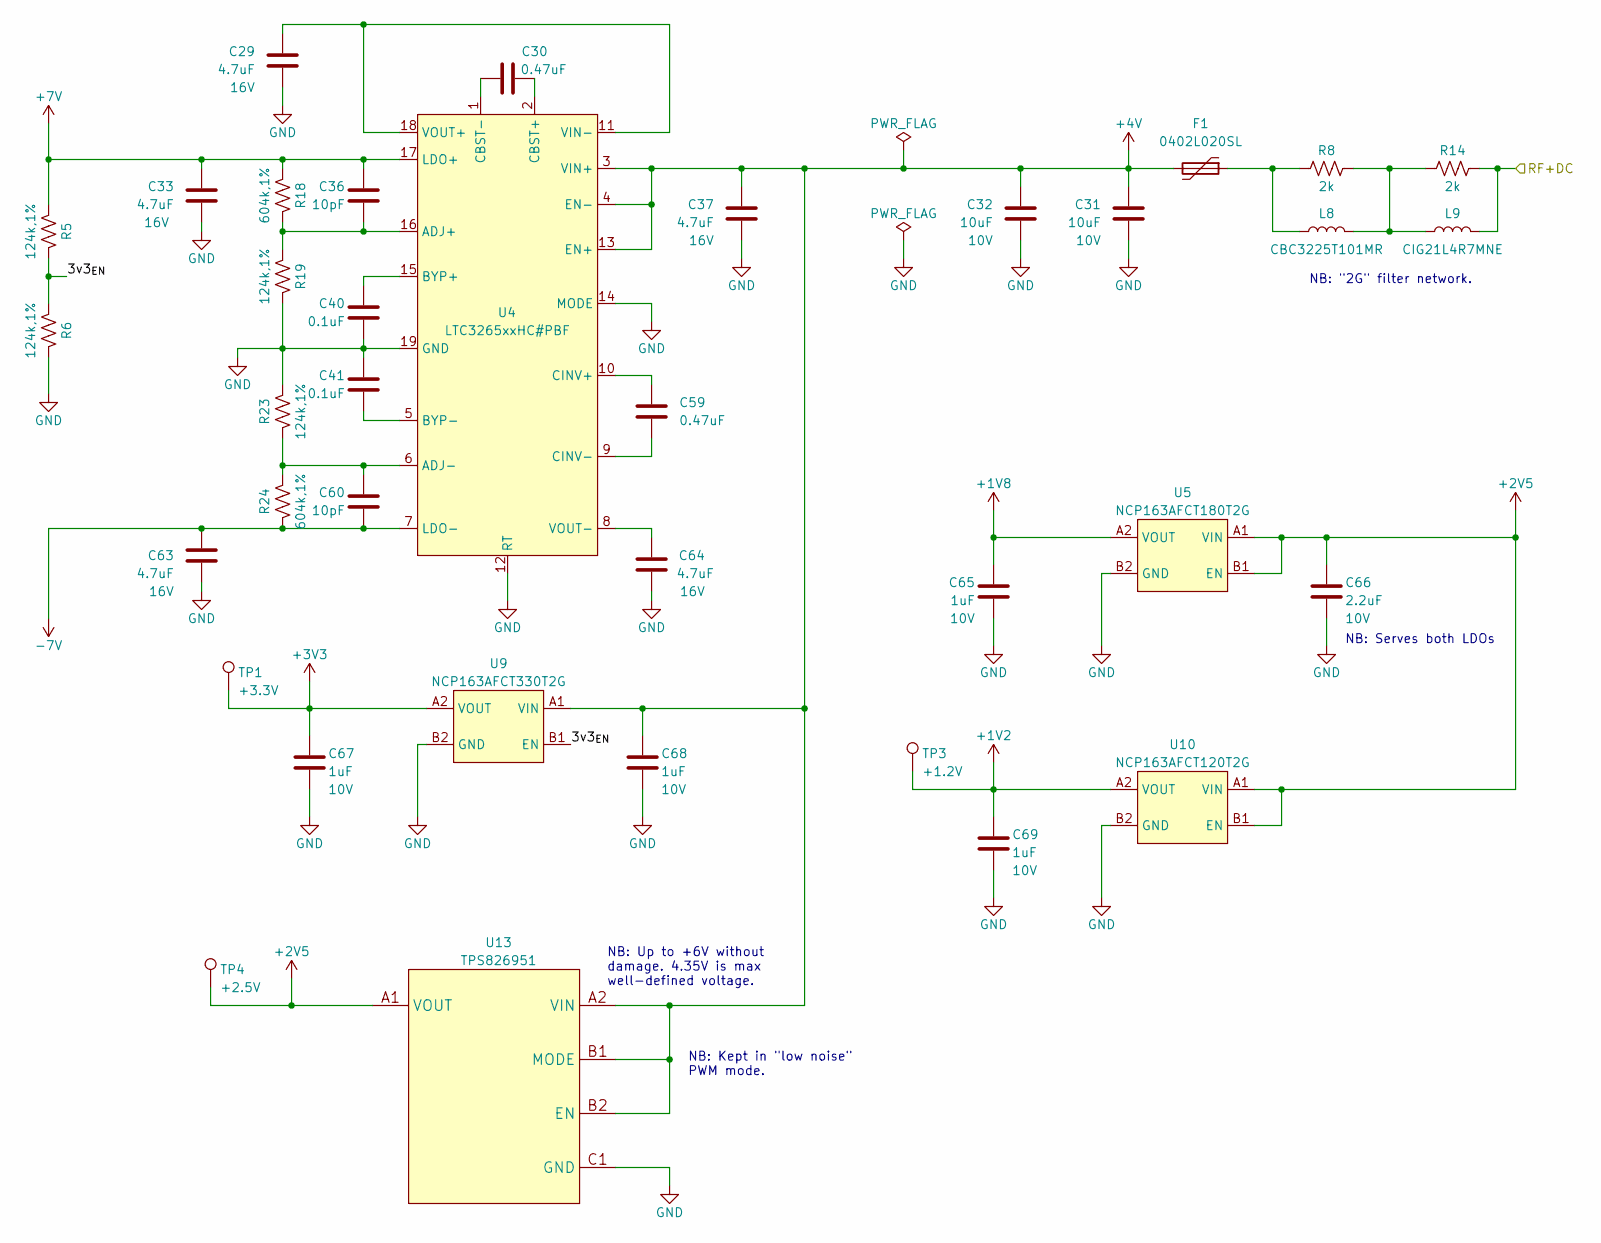
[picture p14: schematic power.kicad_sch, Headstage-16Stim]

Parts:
C29, C33, C37, C63, C64: 4.7uF; C_0402_1005Metric; Voltage 16V
C30, C59: 0.47uF; C_0402_1005Metric; Voltage 35V
C31, C32: 10uF; C_0402_1005Metric; Voltage 10V
C36, C60: 10pF; C_0201_0603Metric; Voltage 50V
C40, C41: 0.1uF; C_0201_0603Metric; Voltage 16V
C65, C67, C68, C69: 1uF; C_0201_0603Metric; Voltage 10V
C66: 2.2uF; C_0201_0603Metric; Voltage 10V
F1: 0402L020SL; LITTLEFUSE_0402
L8: CBC3225T101MR; L_1210_3225Metric
L9: CIG21L4R7MNE; L_0805_2012Metric
R5, R6, R19, R23: 124k,1%; R_0201_0603Metric
R8, R14: 2k; R_0201_0603Metric
R18, R24: 604k,1%; R_0201_0603Metric
TP1: +3.3V; TestPoint_Pad_D0.6mm
TP3: +1.2V; TestPoint_Pad_D0.6mm
TP4: +2.5V; TestPoint_Pad_D0.6mm
U4: LTC3265xxHC#PBF; LINEAR_SON50P300X500X80-19N-D
U5: NCP163AFCT180T2G; ONSEMI_567JZ_WLCSP4-0.64x0.64
U9: NCP163AFCT330T2G; ONSEMI_567JZ_WLCSP4-0.64x0.64
U10: NCP163AFCT120T2G; ONSEMI_567JZ_WLCSP4-0.64x0.64
U13: TPS826951; TI_SIP0008B

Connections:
+1V2: C69.1, TP3.1, U10.A2 (VOUT); also elsewhere on the board
+1V8: C65.1, U5.A2 (VOUT); also elsewhere on the board
+2V5: C66.1, TP4.1, U5.A1 (VIN), U5.B1 (EN), U10.A1 (VIN), U10.B1 (EN), U13.A1 (VOUT); also elsewhere on the board
+3V3: C67.1, TP1.1, U9.A2 (VOUT); also elsewhere on the board
+4V: C31.2, C32.2, C37.2, C68.1, F1.2, U4.3 (VIN+), U4.4 (EN-), U4.13 (EN+), U9.A1 (VIN), U13.A2 (VIN), U13.A3 (VIN), U13.B1 (MODE), U13.B2 (EN)
+7V: C33.2, C36.1, R5.2, R18.2, U4.17 (LDO+); also elsewhere on the board
-7V: C60.2, C63.2, R24.2, U4.7 (LDO-); also elsewhere on the board
/DC Tap & Regulation/3v3_{EN}: R5.1, R6.2, U9.B1 (EN)
/DC Tap & Regulation/RF+DC: L9.1, R14.2; also elsewhere on the board
GND: C29.1, C31.1, C32.1, C33.1, C37.1, C40.2, C41.1, C63.1, C64.1, C65.2, C66.2, C67.2, C68.2, C69.2, R6.1, R19.1, R23.1, U4.12 (RT), U4.14 (MODE), U4.19 (GND), U5.B2 (GND), U9.B2 (GND), U10.B2 (GND), U13.C1 (GND), U13.C2 (GND), U13.C3 (GND); also elsewhere on the board
unnamed: F1.1, L8.1, R8.1
unnamed: L8.2, L9.2, R8.2, R14.1
unnamed: C36.2, R18.1, R19.2, U4.16 (ADJ+)
unnamed: C60.1, R23.2, R24.1, U4.6 (ADJ-)
unnamed: C40.1, U4.15 (BYP+)
unnamed: C41.2, U4.5 (BYP-)
unnamed: C30.1, U4.2 (CBST+)
unnamed: C30.2, U4.1 (CBST-)
unnamed: C59.2, U4.10 (CINV+)
unnamed: C59.1, U4.9 (CINV-)
unnamed: C29.2, U4.11 (VIN-), U4.18 (VOUT+)
unnamed: C64.2, U4.8 (VOUT-)

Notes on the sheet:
NB: Up to +6V without damage. 4.35V is max well-defined voltage.
NB: "2G" filter network.
NB: Serves both LDOs
NB: Kept in "low noise" PWM mode.

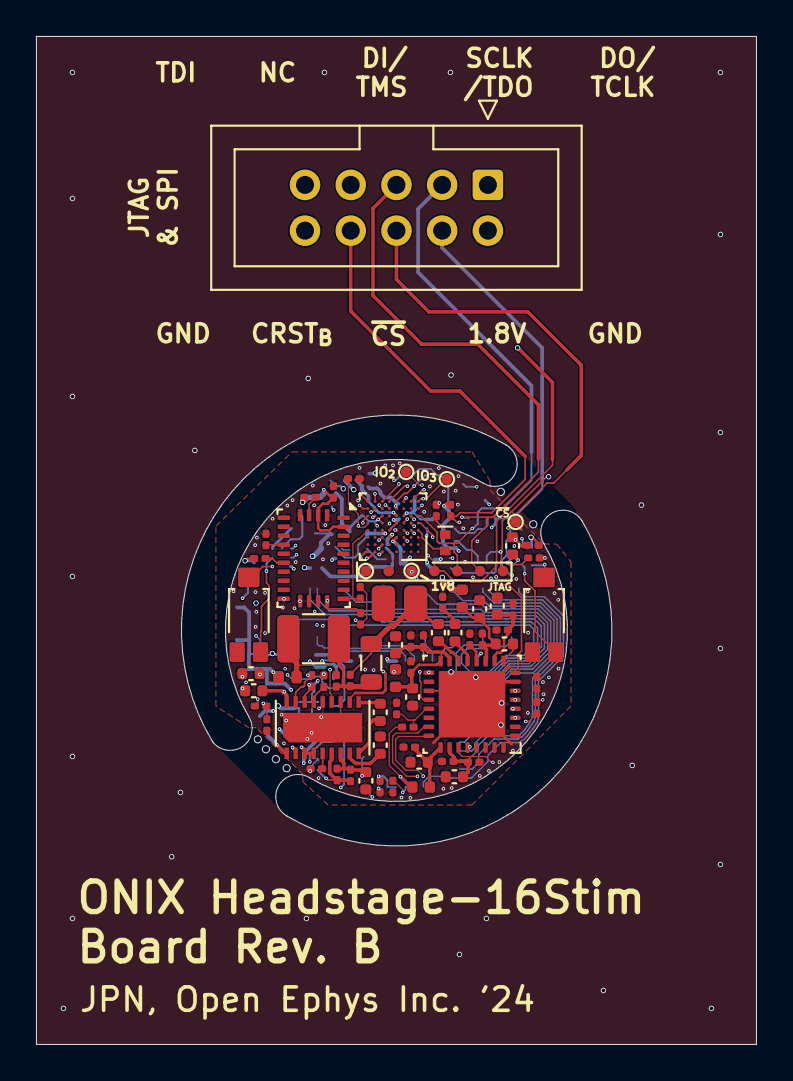
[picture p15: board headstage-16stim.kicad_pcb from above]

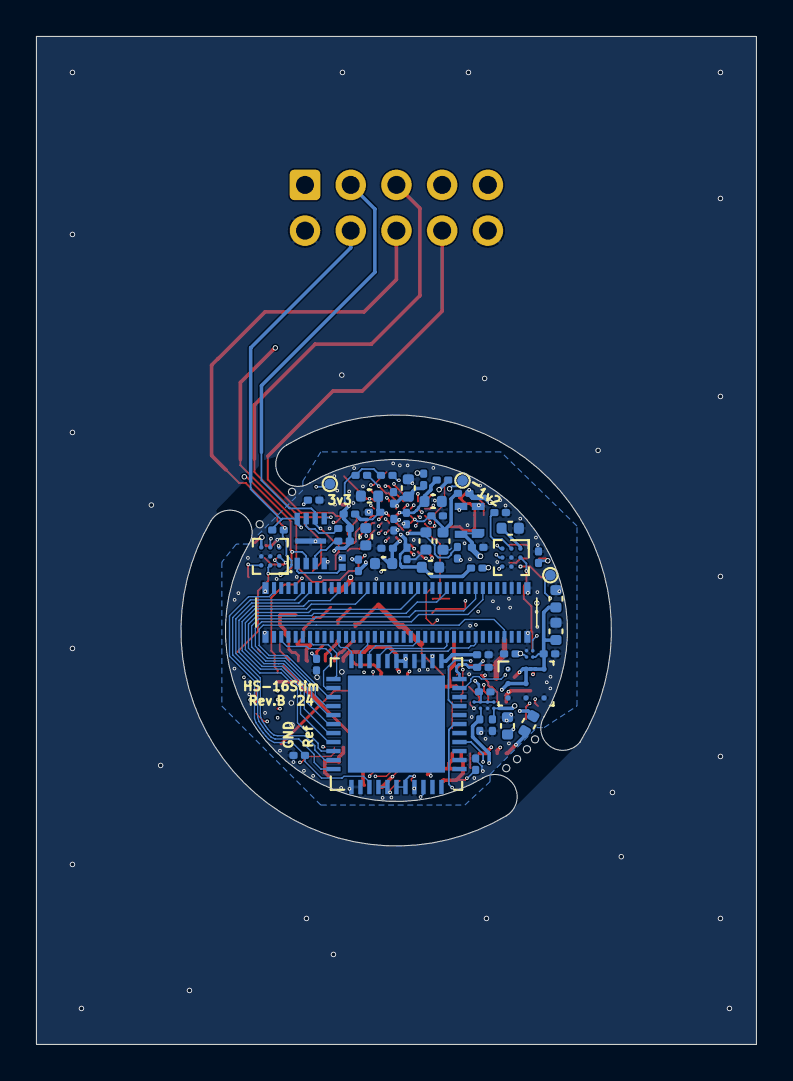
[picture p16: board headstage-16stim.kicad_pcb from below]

Board: 6 copper layers, 40.0 x 56.0 mm, 131 parts (60 on the bottom side), 104 nets.

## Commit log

2022-12-05 Initial commit
    - Sending to speedy for quote and iteration
    [3d-pose.kicad_sch, ephys.kicad_sch, fpga.kicad_sch, headstage-16stim-B_Cu.gbl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]
2022-12-05 Move BOM folder to manufacturing folder
    - Remove redundant gerber PNP files and replace with CSVs
    - Update html BOM to include TempCo
    [headstage-16stim-bottom-pos.csv, headstage-16stim-pnp_bottom.gbr, headstage-16stim-pnp_top.gbr, headstage-16stim-top-pos.csv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]
2023-01-05 PCB Revision A
    - Added production files from Speedy
    [headstage-16stim.kicad_pcb, headstage-16stim.kicad_sch, serializer.kicad_sch]
2024-10-01 Revision B
    - Bring in changes from headstage-rhs116 rev. C that should make this design
    fully functional
    [3d-pose.kicad_sch, ephys.kicad_sch, fpga.kicad_sch, headstage-16stim-B_Cu.gbl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]
